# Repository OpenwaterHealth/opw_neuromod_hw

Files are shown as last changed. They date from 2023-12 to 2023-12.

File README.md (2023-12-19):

# Open-TFUS Neuromodulation Platform
This repository contains the hardware designs and instructions for OpenWater's Transcranial Focused Ultrasound Platform. Open-TFUS is an ultrasound platform designed to help researchers transmit focused ultrasound beams into subject’s brains, so that those researchers can learn more about how different types of ultrasound beams interact with the neurons in the brain. Unlike other focused ultrasound systems which are aimed only by their placement on the head, Open-TFUS uses an array to precisely steer the ultrasound focus to the target location, while its wearable small size allows transmission through the forehead into the brain at a precise spot even when the patient is moving.

For additional details on open-tFUS and its applications, refer to the [wiki](https://wiki.openwater.health/index.php/Openwater_Wiki#Neuromodulation).

# Getting Started
To setup an open-TFUS system, you'll need to follow the assembly instructions contained in this repository. You will also need to download and install the software found in this repository: [opw_neuromod_sw](https://github.com/OpenwaterHealth/opw_neuromod_sw)

# License
This project is licensed under the GNU Affero General Public License v3.0. See [LICENSE](LICENSE) for details.

# Contributing
See [Contributor Guidelines](Contributor-Guidelines) for details.

# Investigational Use Only
CAUTION - Investigational device. Limited by Federal (or United States) law to investigational use. The system described here has *not* been evaluated by the FDA and is not designed for the treatment or diagnosis of any disease. It is provided AS-IS, with no warranties. User assumes all liability and responsibility for identifying and mitigating risks associated with using this software.

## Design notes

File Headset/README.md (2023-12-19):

# Headset Hardware
## Headset
- `7000-0263.EASM`: eDrawing
- `7000-0263.pdf`: PDF Drawing
- `7000-0263.zip`: Parts Archive
- [Headset_Assembly.pdf](Headset_Assembly.pdf): Assembly Instructions
## Hydrogel Standoff
- `3000-0605 HYDROGEL, WEDGED, AS CAST.eprt`: Hydrogel standoff model
## Foam Pads
- `3000-0763.pdf`: Adhesive-backed foam pad for nose bridge
- `3000-0764.pdf`: Adhesive-backed foam pad for forehead

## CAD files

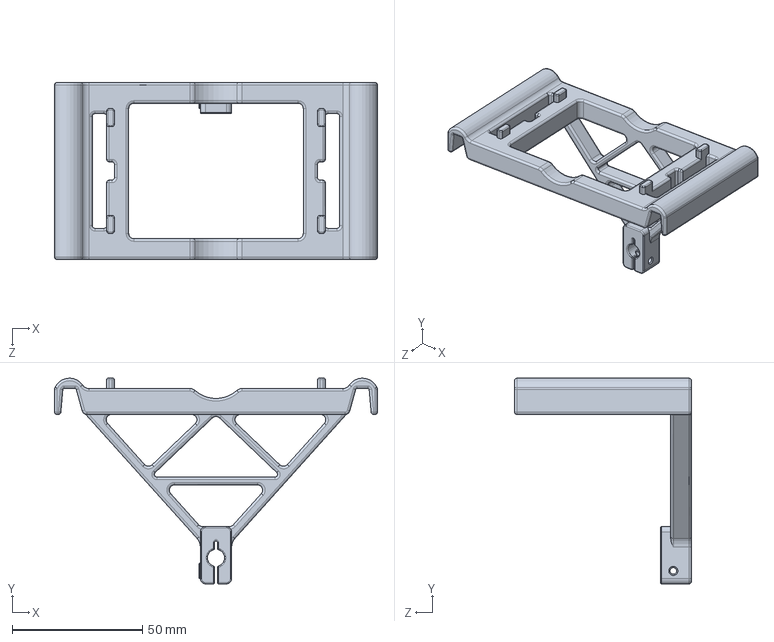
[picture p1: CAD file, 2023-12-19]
Acoustic Validation/TRANSDUCER SUPPORT FRAME.SLDPRT
124.0 x 79.0 x 68.0 mm

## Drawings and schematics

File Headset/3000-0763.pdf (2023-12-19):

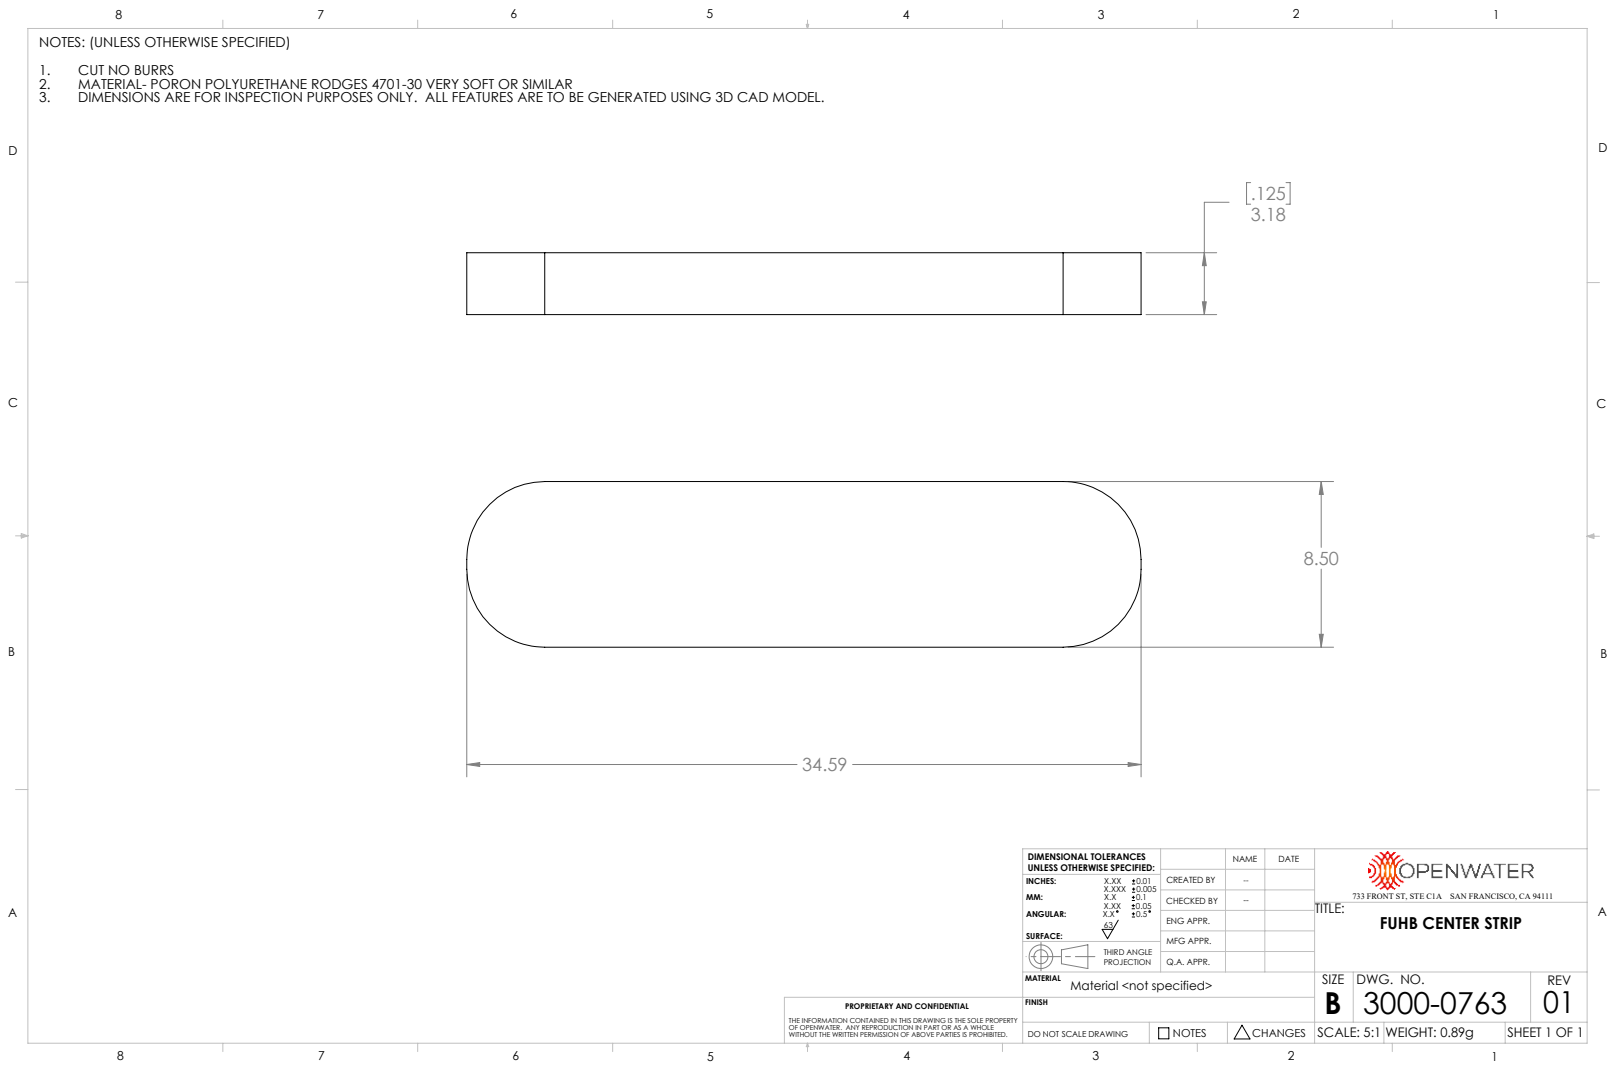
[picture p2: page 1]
X.XXX 0.005; CREATED BY; CHECKED BY; ENG APPR.; MFG APPR.; Q.A. APPR.; DWG. NO.; REV; SCALE: 5:1 WEIGHT: 0.89g; DO NOT SCALE DRAWING; SHEET 1 OF 1

NOTES: (UNLESS OTHERWISE SPECIFIED)
1. CUT NO BURRS
2. MATERIAL- PORON POLYURETHANE RODGES 4701-30 VERY SOFT OR SIMILAR
3. DIMENSIONS ARE FOR INSPECTION PURPOSES ONLY. ALL FEATURES ARE TO BE GENERATED USING 3D CAD MODEL.

DIMENSIONAL TOLERANCES
UNLESS OTHERWISE SPECIFIED:
SURFACE:

733 FRONT ST, STE C1A SAN FRANCISCO, CA 94111
TITLE:
FUHB CENTER STRIP

THIRD ANGLE
PROJECTION
Material <not specified>

PROPRIETARY AND CONFIDENTIAL

THE INFORMATION CONTAINED IN THIS DRAWING IS THE SOLE PROPERTY
OF OPENWATER. ANY REPRODUCTION IN PART OR AS A WHOLE
WITHOUT THE WRITTEN PERMISSION OF ABOVE PARTIES IS PROHIBITED.

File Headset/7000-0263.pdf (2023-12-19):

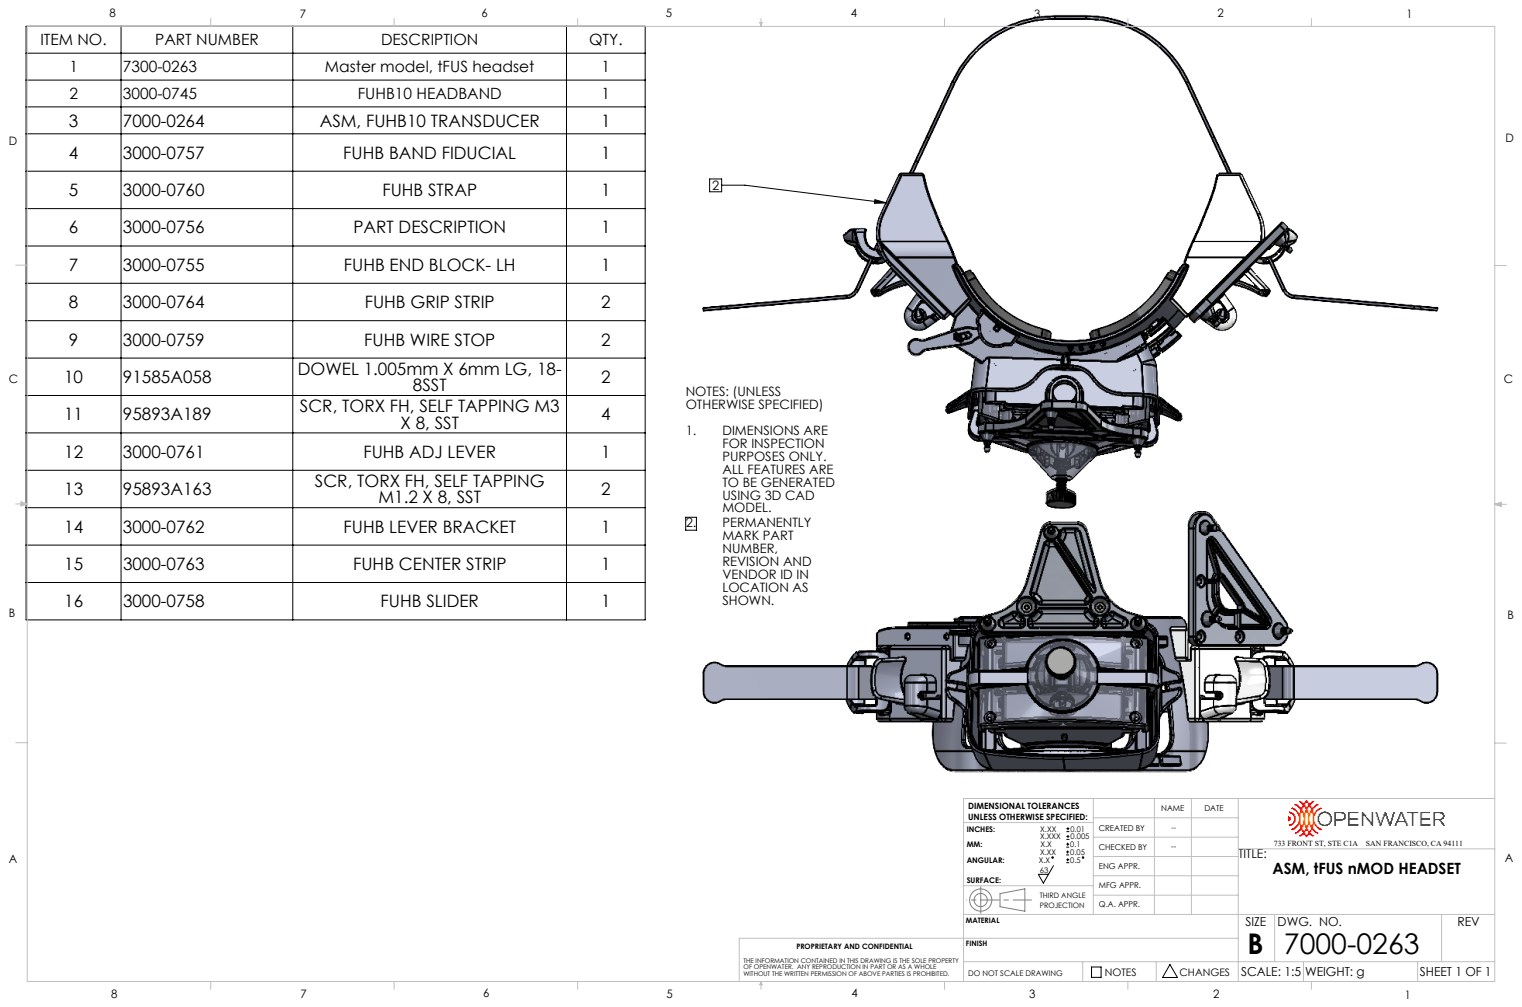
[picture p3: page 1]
X.XXX 0.005; THIRD ANGLE; CREATED BY; CHECKED BY; ENG APPR.; MFG APPR.; Q.A. APPR.; DWG. NO.; REV; SCALE: 1:5 WEIGHT: g; DO NOT SCALE DRAWING; SHEET 1 OF 1

ITEM NO. | PART NUMBER | DESCRIPTION | QTY.
1 | 7300-0263 | Master model, tFUS headset | 1
2 | 3000-0745 | FUHB10 HEADBAND | 1
3 | 7000-0264 | ASM, FUHB10 TRANSDUCER | 1
4 | 3000-0757 | FUHB BAND FIDUCIAL | 1
5 | 3000-0760 | FUHB STRAP | 1
6 | 3000-0756 | PART DESCRIPTION | 1
7 | 3000-0755 | FUHB END BLOCK- LH | 1
8 | 3000-0764 | FUHB GRIP STRIP | 2
9 | 3000-0759 | FUHB WIRE STOP | 2
10 | 91585A058 | DOWEL 1.005mm X 6mm LG, 18-8SST | 2
11 | 95893A189 | SCR, TORX FH, SELF TAPPING M3 X 8, SST | 4

NOTES: (UNLESS
OTHERWISE SPECIFIED)
1. DIMENSIONS ARE
FOR INSPECTION
PURPOSES ONLY.
ALL FEATURES ARE
TO BE GENERATED
USING 3D CAD
MODEL.
2. PERMANENTLY
MARK PART
NUMBER,
REVISION AND
VENDOR ID IN
LOCATION AS
SHOWN.

12 | 3000-0761 | FUHB ADJ LEVER | 1
13 | 95893A163 | SCR, TORX FH, SELF TAPPING M1.2 X 8, SST | 2

14 | 3000-0762 | FUHB LEVER BRACKET | 1
15 | 3000-0763 | FUHB CENTER STRIP | 1
16 | 3000-0758 | FUHB SLIDER | 1

DIMENSIONAL TOLERANCES
UNLESS OTHERWISE SPECIFIED:
SURFACE:

733 FRONT ST, STE C1A SAN FRANCISCO, CA 94111
TITLE:
ASM, tFUS nMOD HEADSET

PROPRIETARY AND CONFIDENTIAL

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

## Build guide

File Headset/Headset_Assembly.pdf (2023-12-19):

# Ultrasound headset assy

PH 7/5/2023

## Step 1

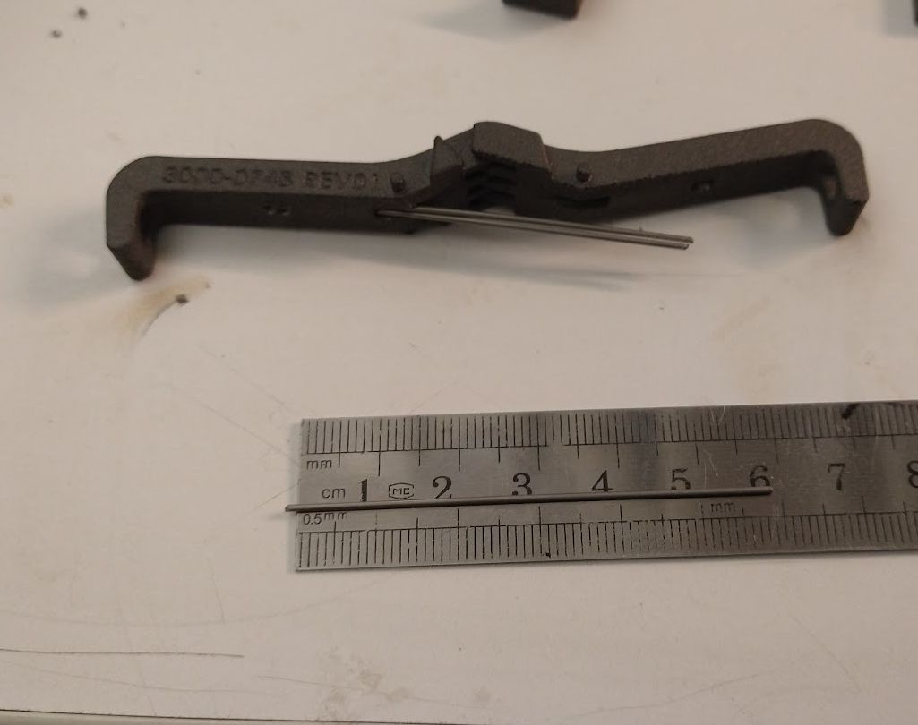
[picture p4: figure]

- Cut two wires to
58-59 mm
- Insert both to lever
arms

## Step 2

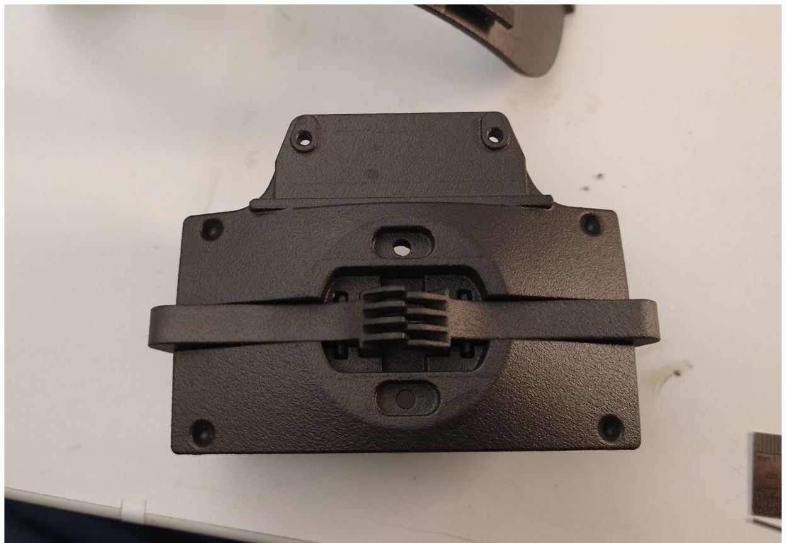
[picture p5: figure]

- Load arms into
transducer base

## Step 3

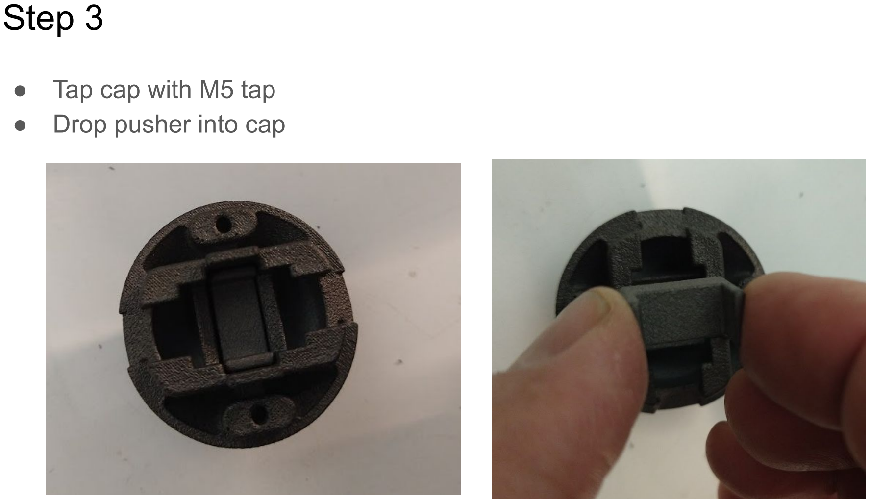
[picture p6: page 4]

- Tap cap with M5 tap
- Drop pusher into cap

## Step 4

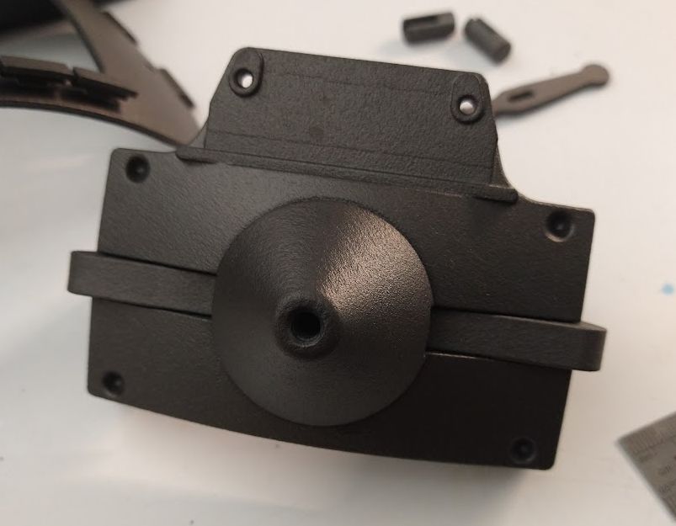
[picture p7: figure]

- Lower cap on to
housing base

## Step 5

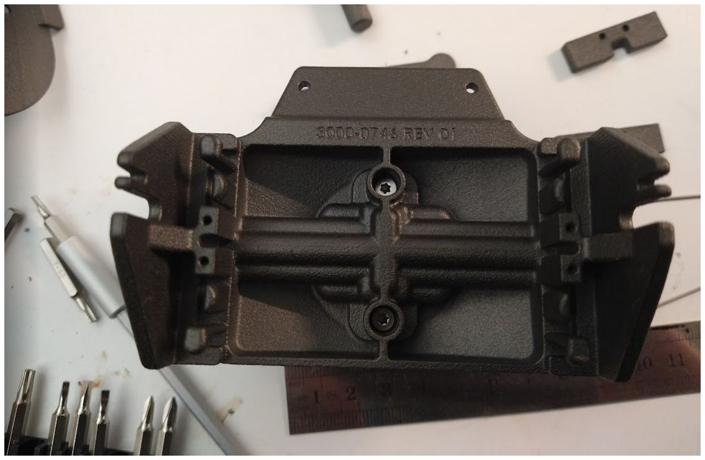
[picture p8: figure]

- Screw cap on to
the base from the
back side using
M3 plastic screw
- Screw with T-10
star torque head
driver

## Step 6

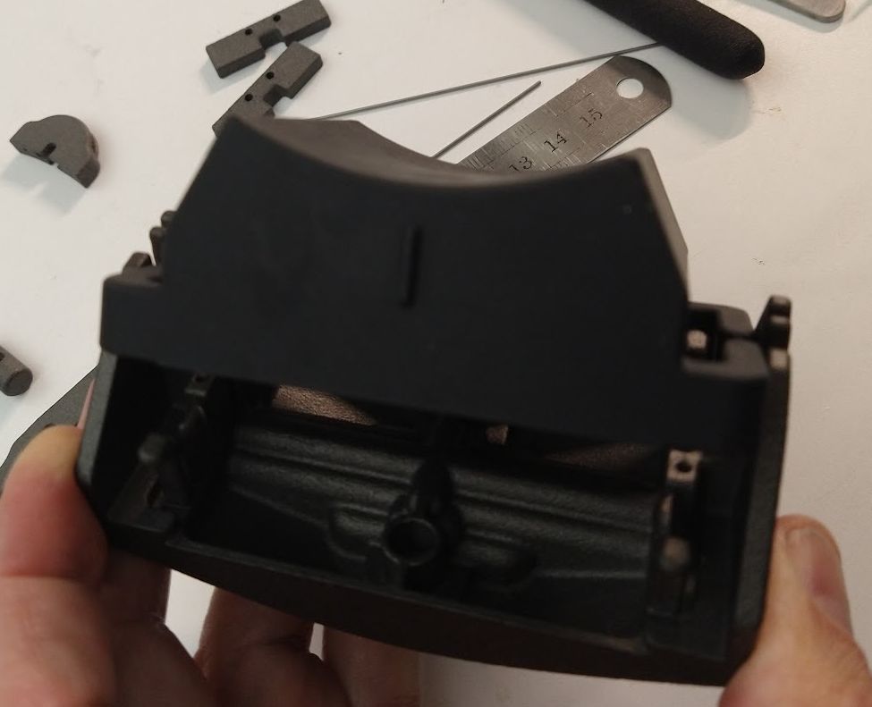
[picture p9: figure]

- Place transducer on the
back housing
- Lay in with a tilt first
●

## Step 7

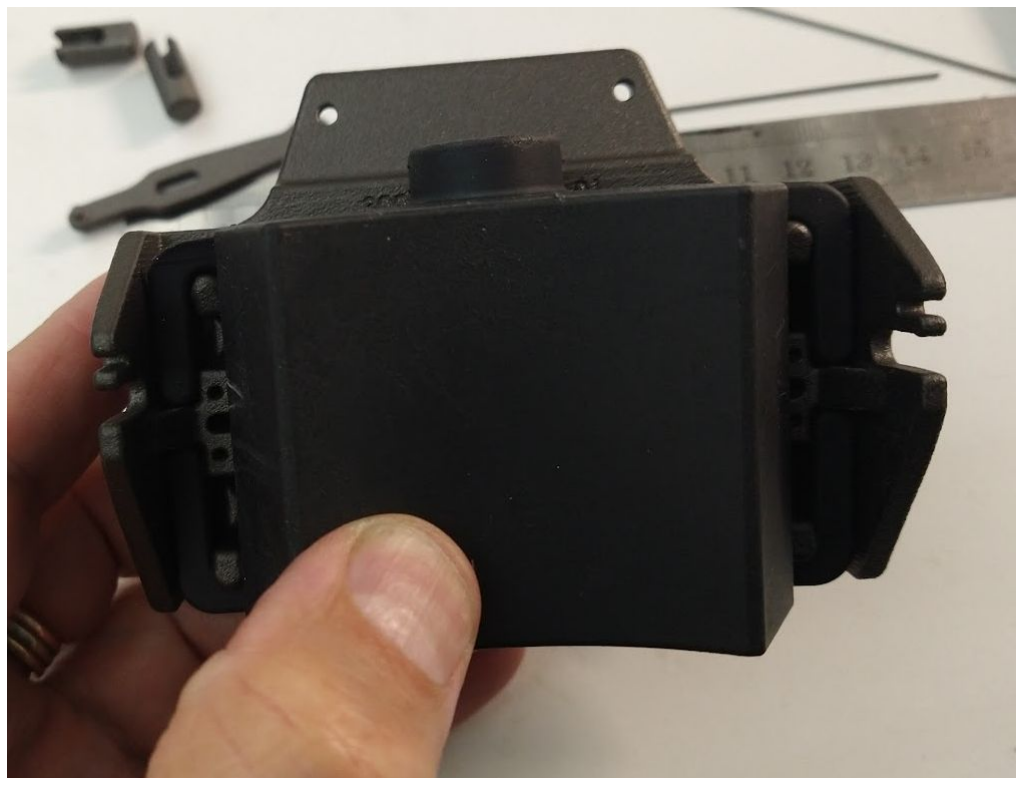
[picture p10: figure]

- Push back base housing
transducer snaps
- Push in transducer flat until snaps engage

## Step 8

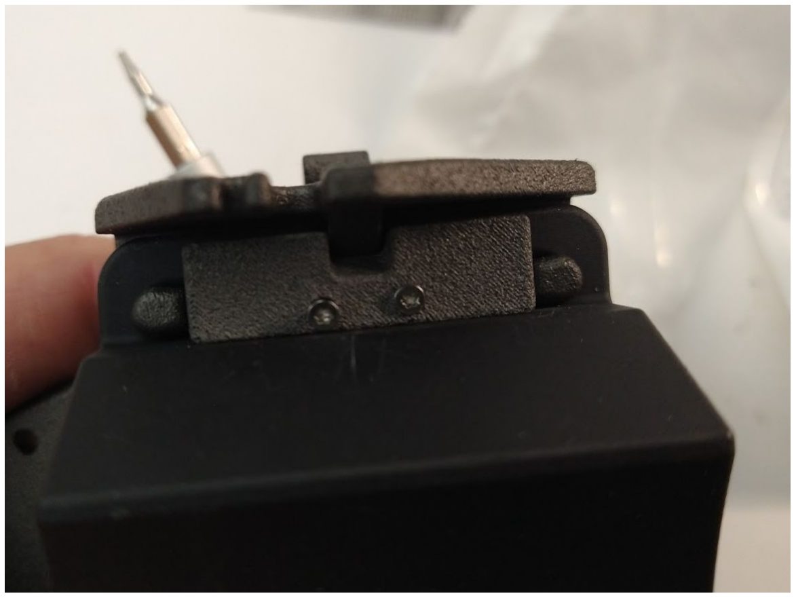
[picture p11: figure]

- Secure with transducer
secure straps
- Place M1.6 screws
- Screw with T-5 torque
driver

## Step 9

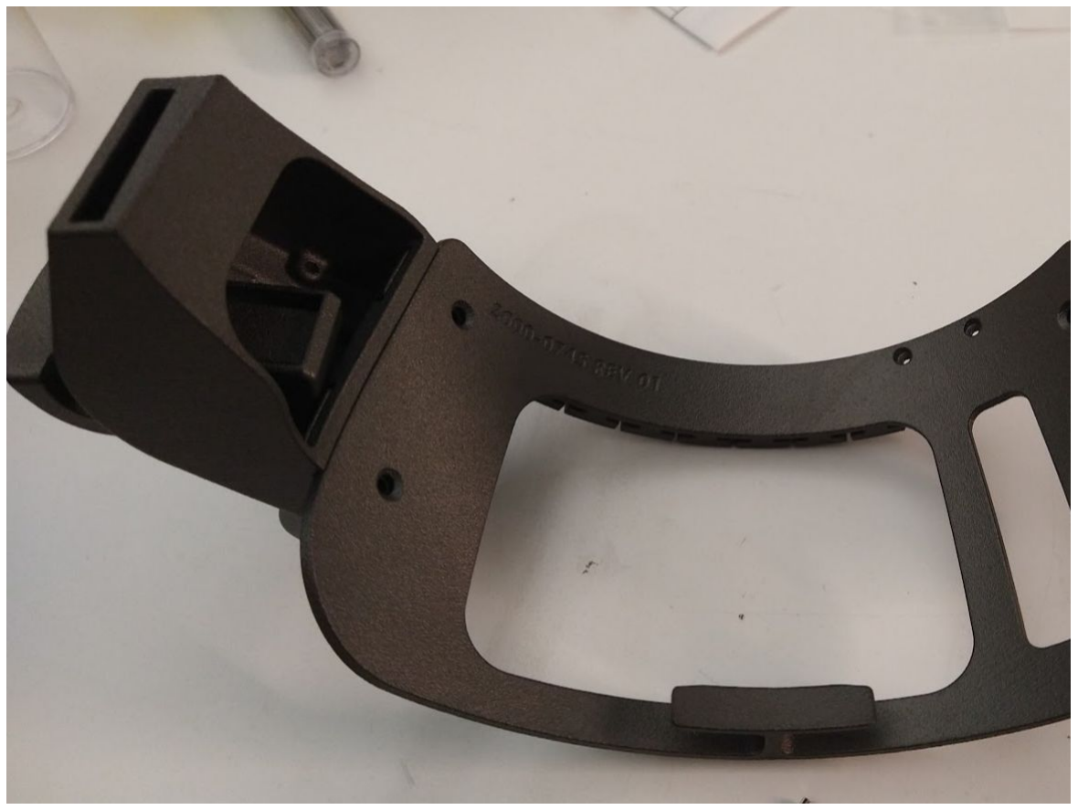
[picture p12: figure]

- Attach one side of the
end block to the
Headband

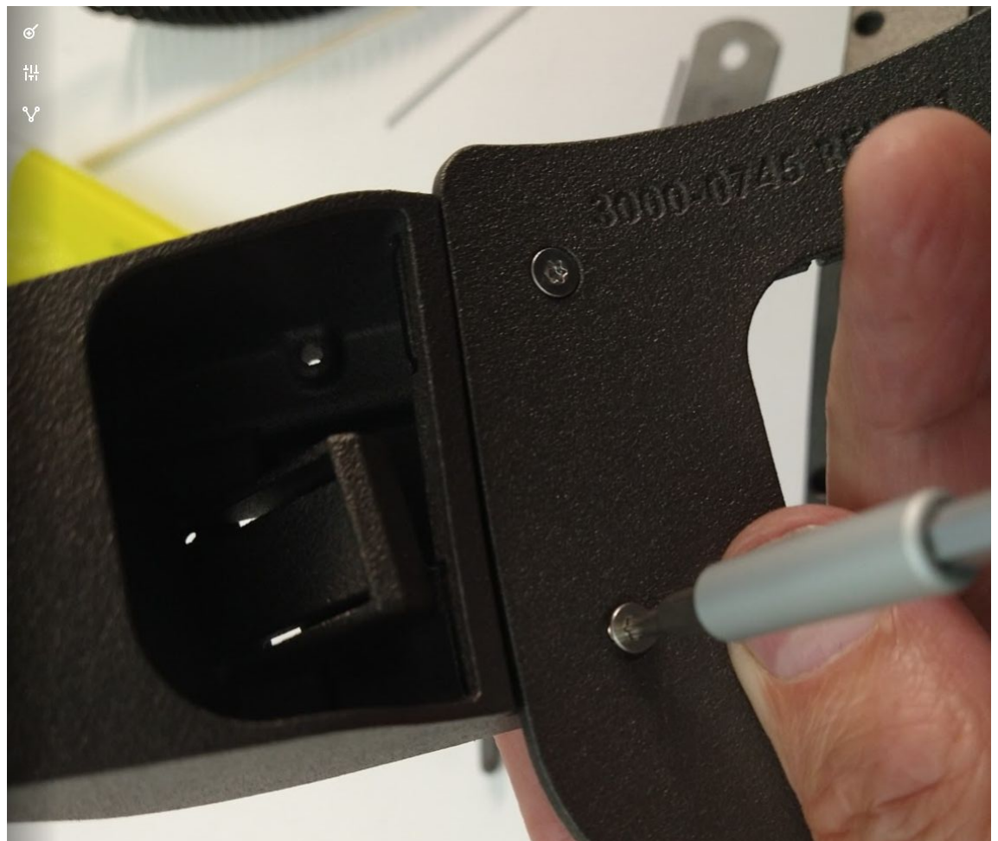
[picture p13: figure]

## Step 10

- Screw 2 M3 screws
to secure end block

## Step 11

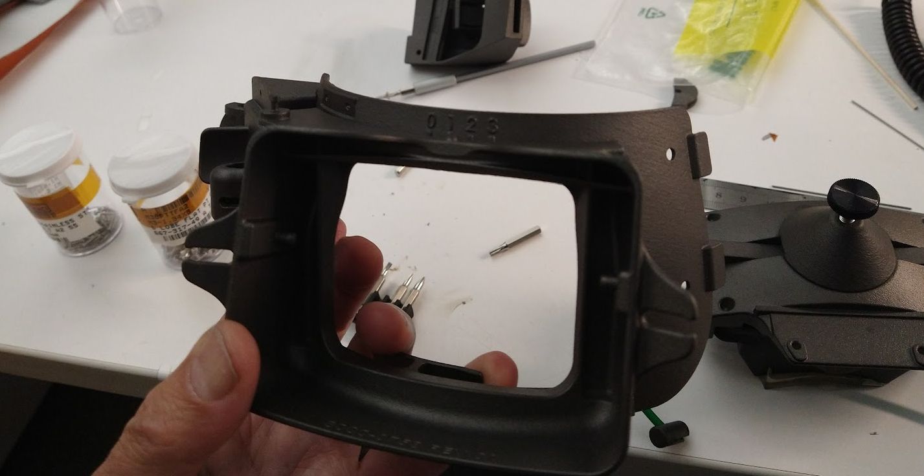
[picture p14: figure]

- Load FUHB
slider to
headband
tracks

## Step 12

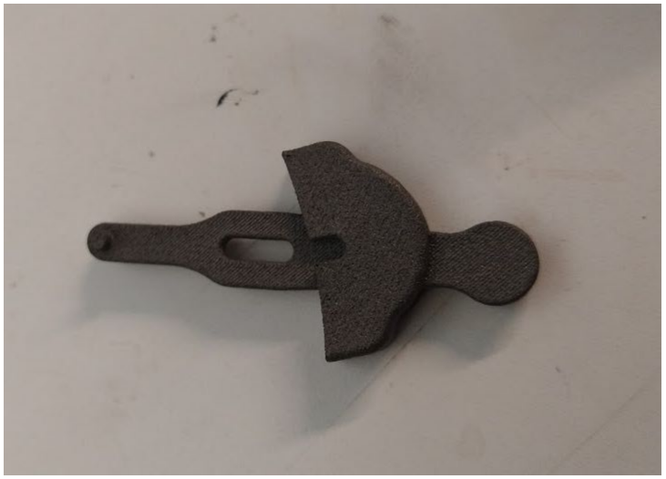
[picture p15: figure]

- Assembly lever
bracket to lever

## Step 13

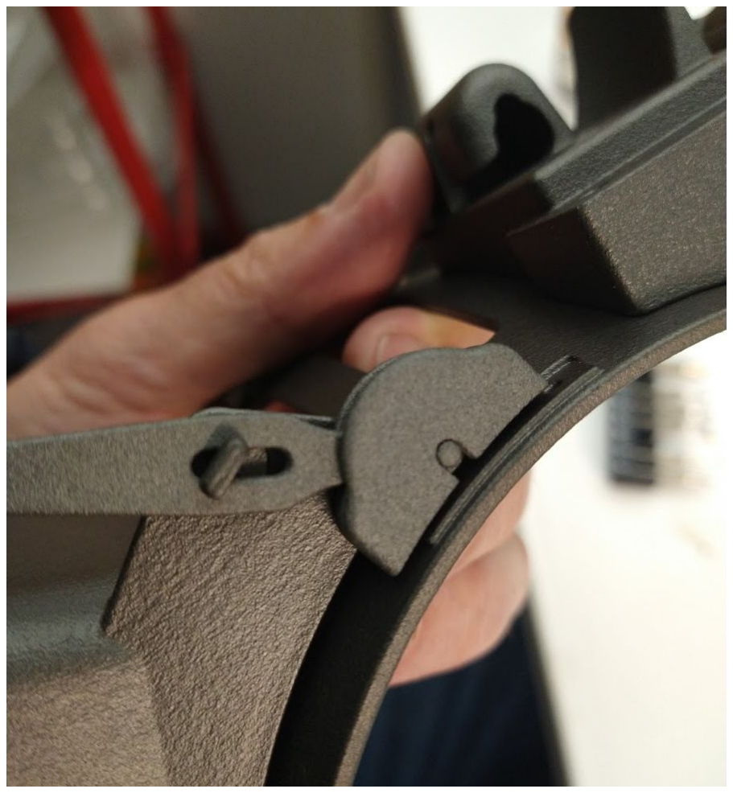
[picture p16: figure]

- Add lever assembly to headband

## Step 14

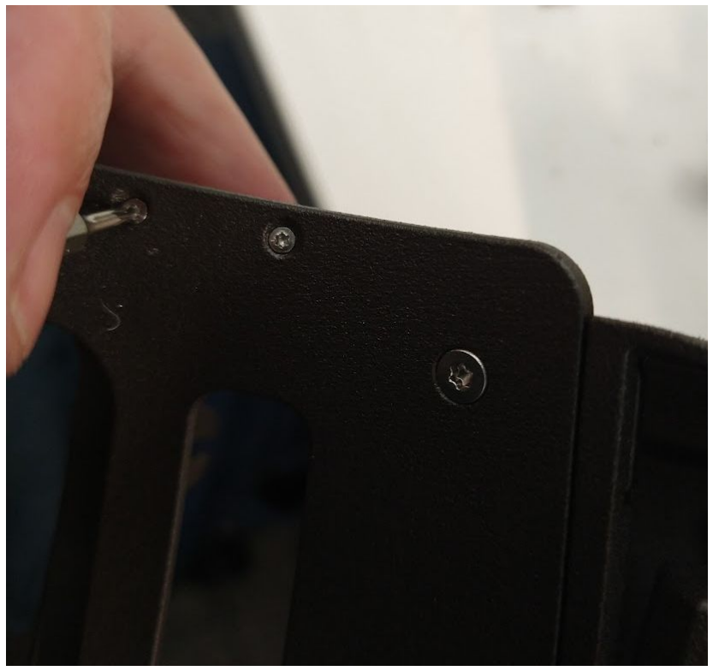
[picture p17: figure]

- Screw bracket to the headband from the backside with the 1.6 mm screws

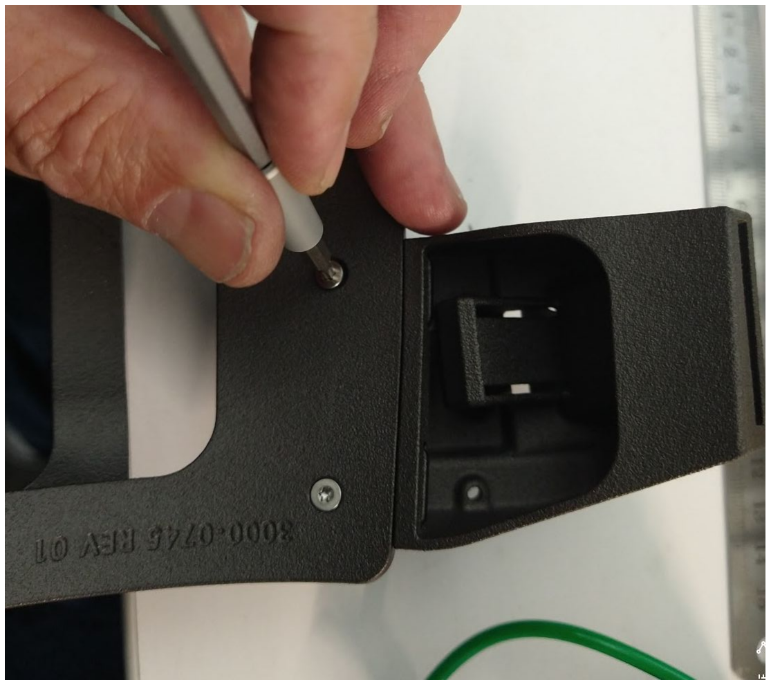
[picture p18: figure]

## Step 15

- Screw on the second
end block

## Step 16

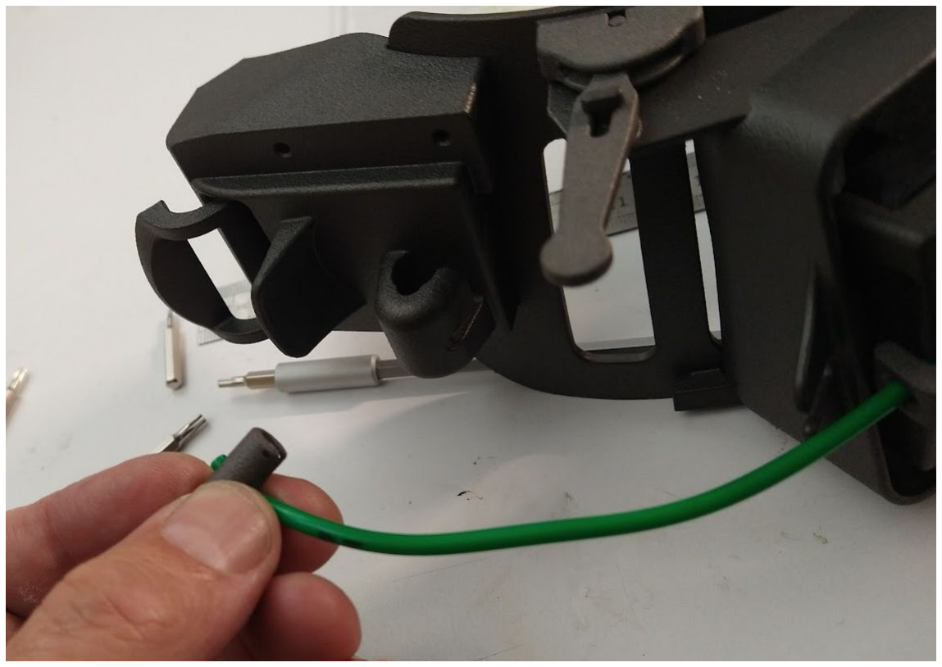
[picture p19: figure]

- Thread slippery
cord though levers
and end nut

Ordered tube was wrong
should reorder

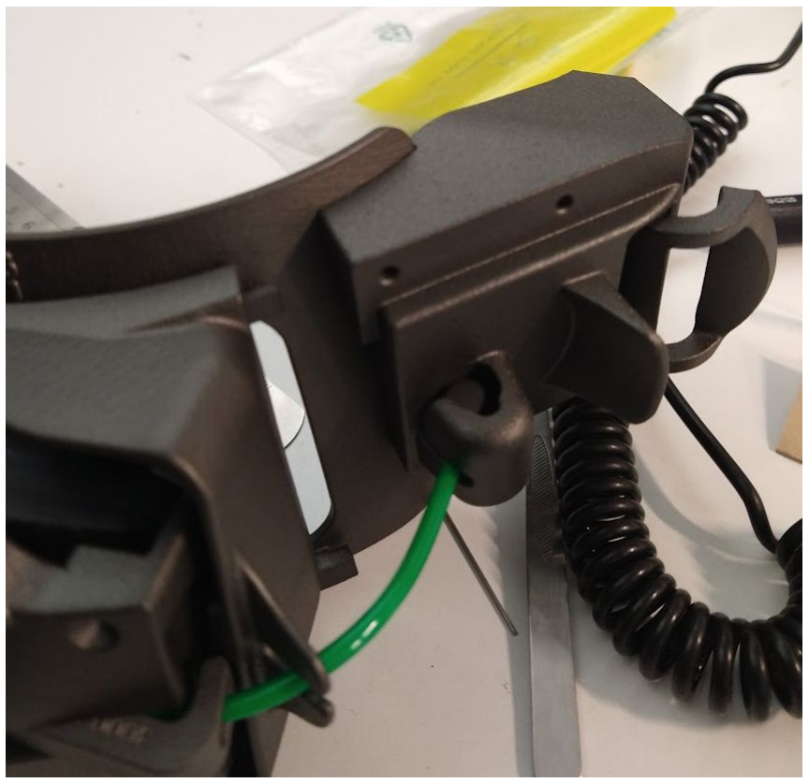
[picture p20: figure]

## Step 17

- Insert nut into endblock slot

## Step 18

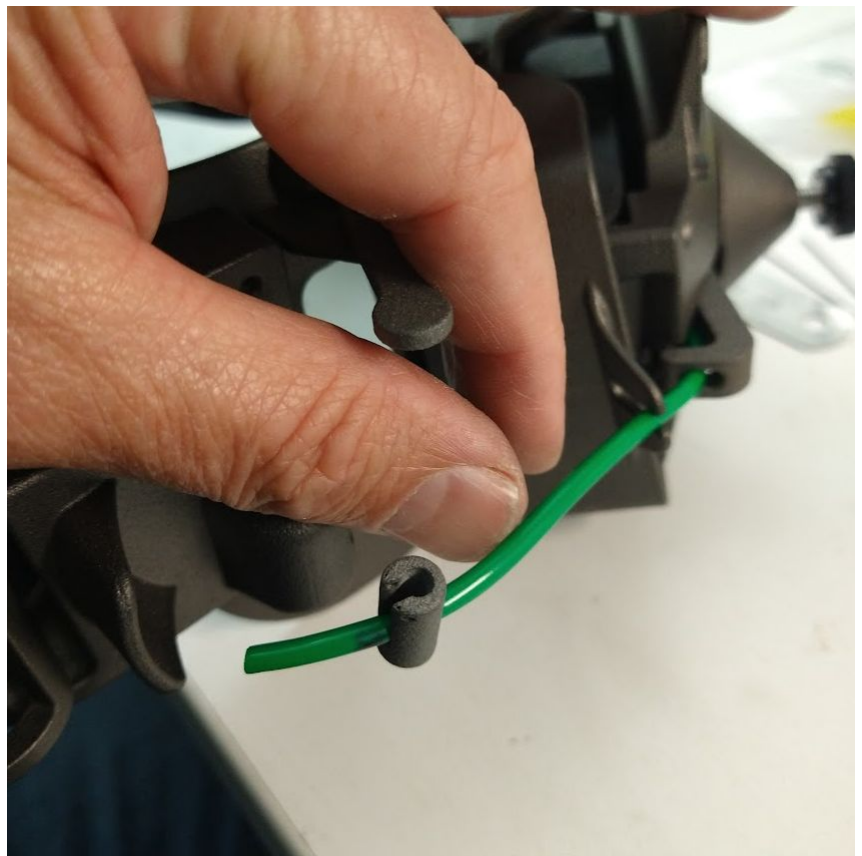
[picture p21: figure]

- Install endblock on
other side

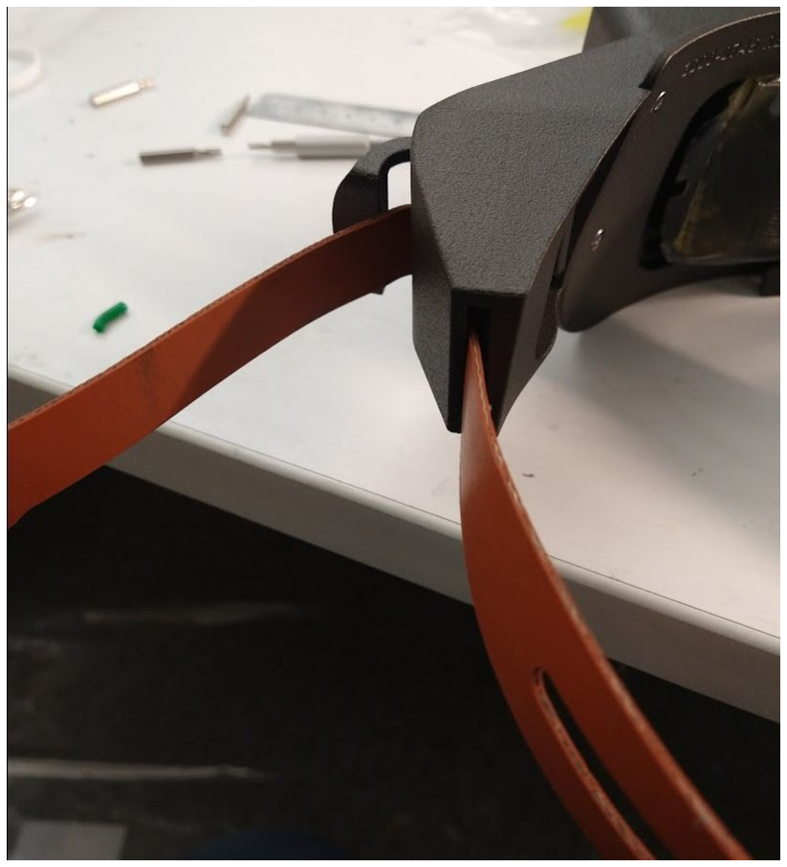
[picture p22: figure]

## Step 19

- Thread strap end first

Extra straps not found, order more

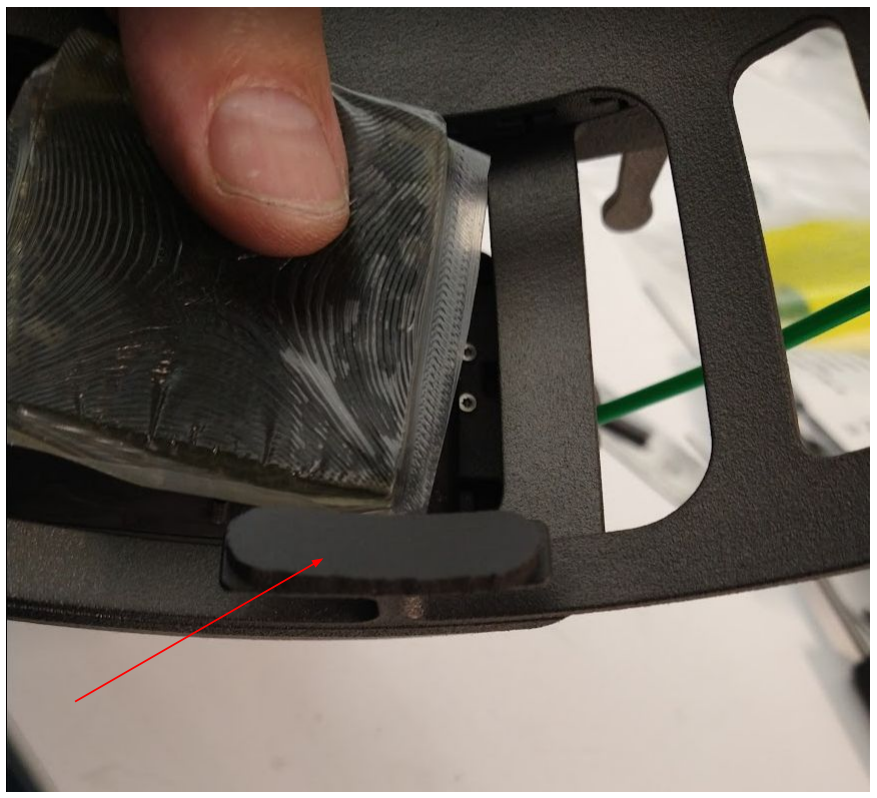
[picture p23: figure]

## Step 20

- Add center foam pad

PSA not sticky enough

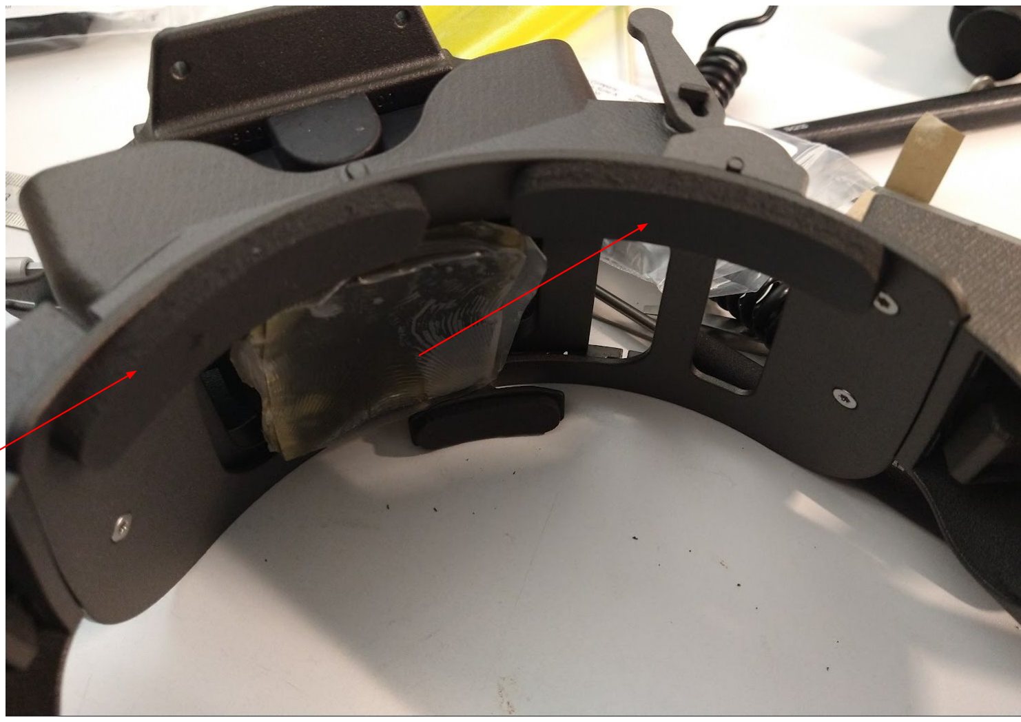
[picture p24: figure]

## Step 21

- Add two foam
pressure pads

PSA not sticky
enough

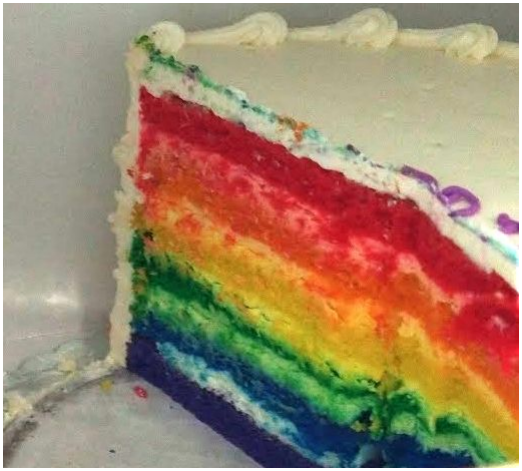
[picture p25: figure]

## Eat cake @ finish line

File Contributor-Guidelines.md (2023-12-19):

[home](Home)

# Contribution Guidelines for Openwater

## Introduction
Welcome to Openwater! We are excited to have you on board and look forward to your contributions. This document is intended to provide a set of guidelines to help you contribute to our project effectively.

## Code of Conduct
Please read our Code of Conduct before contributing. We believe in a respectful and collaborative environment, and our Code of Conduct outlines our expectations for all participants.

## Getting Started
- Fork the Repository: Start by forking the repository to your GitHub account.
- Set Up Your Environment: Follow the setup instructions in the README to get your development environment ready.

## Making Contributions
- Issues: Before creating new issues, please check if the issue already exists to avoid duplicates. When creating an issue, provide a clear and detailed description, including steps to reproduce, if applicable.
- Pull Requests:
  - Branching: Create a new branch for each feature or fix.
  - Commit Messages: Write clear, concise commit messages with a brief description of the changes.
  - Code Standards: Ensure your code adheres to the project's coding standards and guidelines.
  - Testing: Add relevant tests for your changes and ensure all tests pass.
  - Documentation: Update the documentation to reflect your changes, if necessary.
  - Code Reviews: Once you submit a pull request, the project maintainers will review your changes. Be responsive to feedback and make necessary adjustments.
## Best Practices
- Stay Updated: Regularly sync your fork with the main repository to keep up with the latest changes.
- Communicate: If you're working on a particular issue, let others know to avoid overlapping efforts. Use the project's communication channels for discussions.
- Be Respectful: Respect the time and effort of maintainers and fellow contributors.

## Recognition of Contributions
We value your contributions, and recognition will be given for each contribution. Contributors will be acknowledged in the project's documentation and release notes.

## Asking for Help
If you need help or have any questions, feel free to reach out to the community through [preferred communication channels, e.g., GitHub Discussions, Slack, Mailing List].

## Final Note
Your contributions play a significant role in the success of this project. We are grateful for your willingness to contribute and look forward to your valuable input.

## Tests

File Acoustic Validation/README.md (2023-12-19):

# Acoustic Validation Hardware
This folder contains:
- `TRANSDUCER SUPPORT FRAME.SLDPRT`: 3D printed part that holds the hydrophone and the probe
- `TRANSDUCER TEST STAND(v2023-01-24).easm`: Assembly with probe and tank

Instructions for assembly and use may be found in the user manual.

hydrophone tank and holder for probe and hydrophone
